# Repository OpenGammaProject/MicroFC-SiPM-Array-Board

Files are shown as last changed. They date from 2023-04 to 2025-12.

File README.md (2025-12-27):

# MicroFC SiPM Array Board

Carrier board for a 2 x 2 array of the 6 mm C-Series MICROFC-60035-SMT silicon photomultipliers by [onsemi](https://www.onsemi.com/pdf/datasheet/microc-series-d.pdf).

PCB size is 20 x 20 mm. The solder pads for the SiPM are slightly bigger than they need to so that you can easily hand-solder everything! I set up a project page over at PCBWay with all the files for you to make it hopefully as easy as possible to order (affiliate link).

<a href="https://www.pcbway.com/project/shareproject/MicroFC_SiPM_Array_Board_8e6e9394.html">PCB from PCBWay</a>

<p align="center">
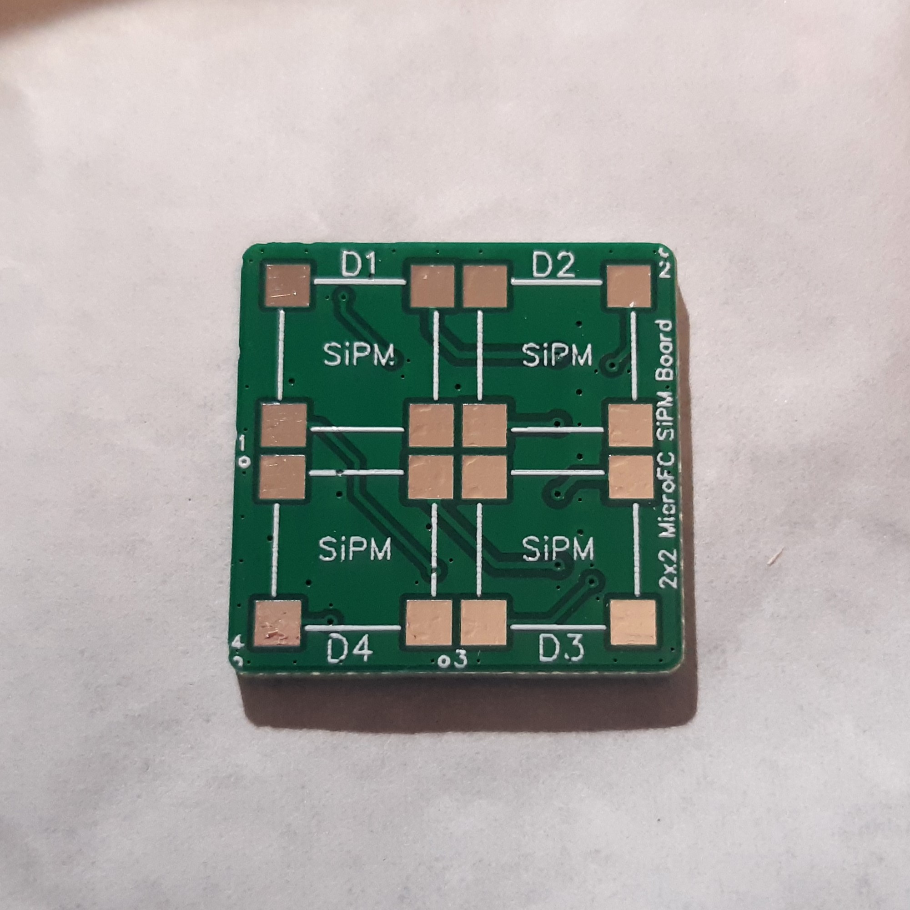
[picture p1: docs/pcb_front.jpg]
Front Side PCB
  
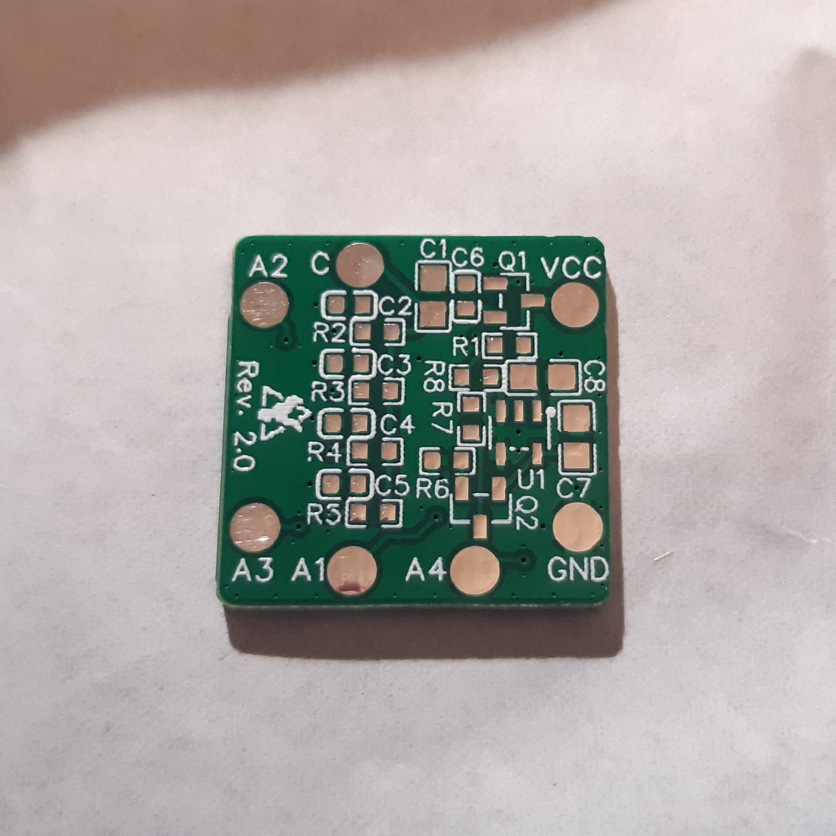
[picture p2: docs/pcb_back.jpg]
Back Side PCB
  
</p>

<p align="center">
  Front Side PCB Rendering
  Back Side PCB Rendering
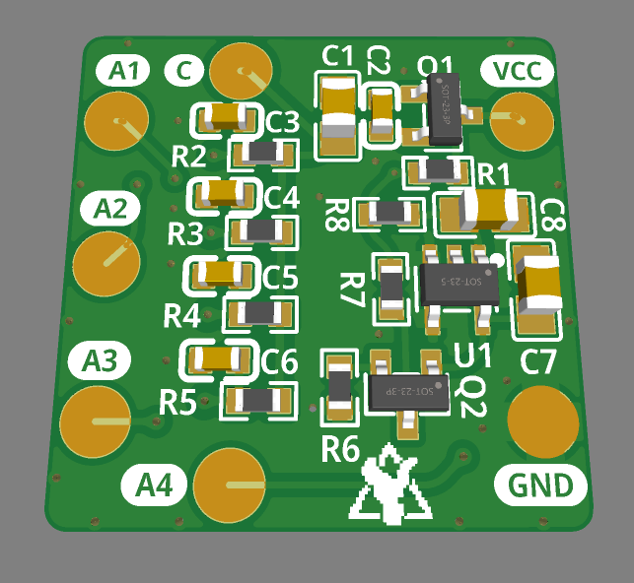
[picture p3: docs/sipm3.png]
Back Side 3D Rendering
  
</p>

On the front side there are only the 4 sensors themselves while all the other parts are on the back. This ensures good optical contact and light-tight sealing. The PCB includes some bias filtering for the 4 SiPMs that must also be soldered and an optional temperature compensation circuit! The temperature compensation takes care of the change in bias voltage and therefore gain depending on the ambient temperature (~21mV/K).

If you want to use the added temperature compensation, be sure to solder all the components to the board and connect your power to the `VCC` pad. For setting the correct voltage, you can check the `C` pad on the PCB, but be sure to do this either before soldering the SiPMs or only when the SiPMs are not exposed to ANY light, otherwise they'll saturate immediately and pass a high current. You can also check the voltage on your power supply itself of course, but due to the nature of the compensation circuitry, the applied voltage to the SiPMs will then be a couple of 100 millivolts lower than what is shown. If you don't want to use the extra circuitry, you can apply your power directly to the `C` pad on the PCB. However, you still need to solder the low-pass filters for that (R2 - R5 and C2 - C5) and C1. The voltage will then be exactly what you apply.

The SiPMs all share a common cathode with bulk decoupling and an R-C low-pass filter each. The anodes are **not** connected together so that you can have some spatial resolution if you want to. You could mount a very small scintillator to each sensor and then have a four pixel gamma-ray camera, yay I guess?!

However, you can also connect all four SiPMs in parallel to a common output by connecting the anode pads to each other, e.g. by connecting the wires that you solder to the pads. You will obviously lose any spatial resolution, but this way you can use it just like a single SiPM in the 4P configuration. SNR should be pretty much the same as with a single SiPM, but your active area will be 4x that of a single one!

To orient the SiPM correctly, look at the notches at the side of the plastic casing. There are 2 lines at the dot right here, that must be matched up with the dot on the PCB. There are numbered dots on the PCB that have to be matched up with that.

<p align="center">
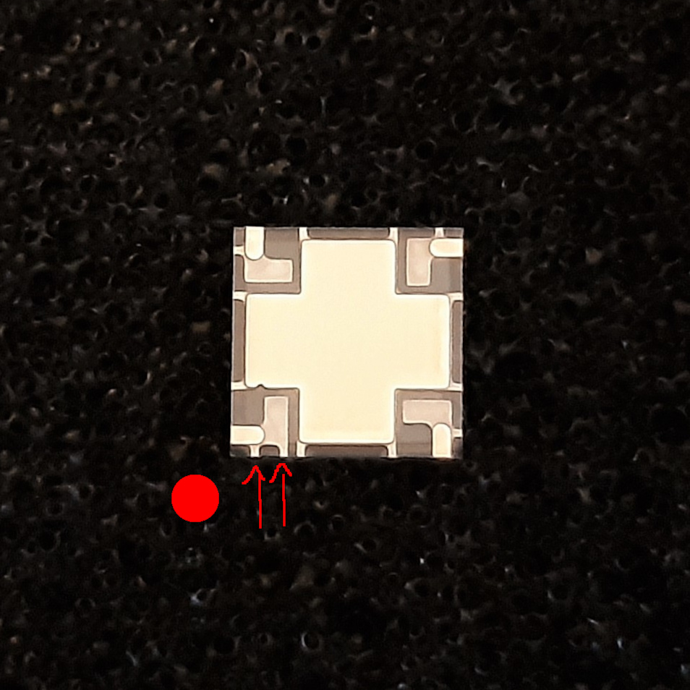
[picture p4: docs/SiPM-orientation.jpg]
SiPM Orientation
  
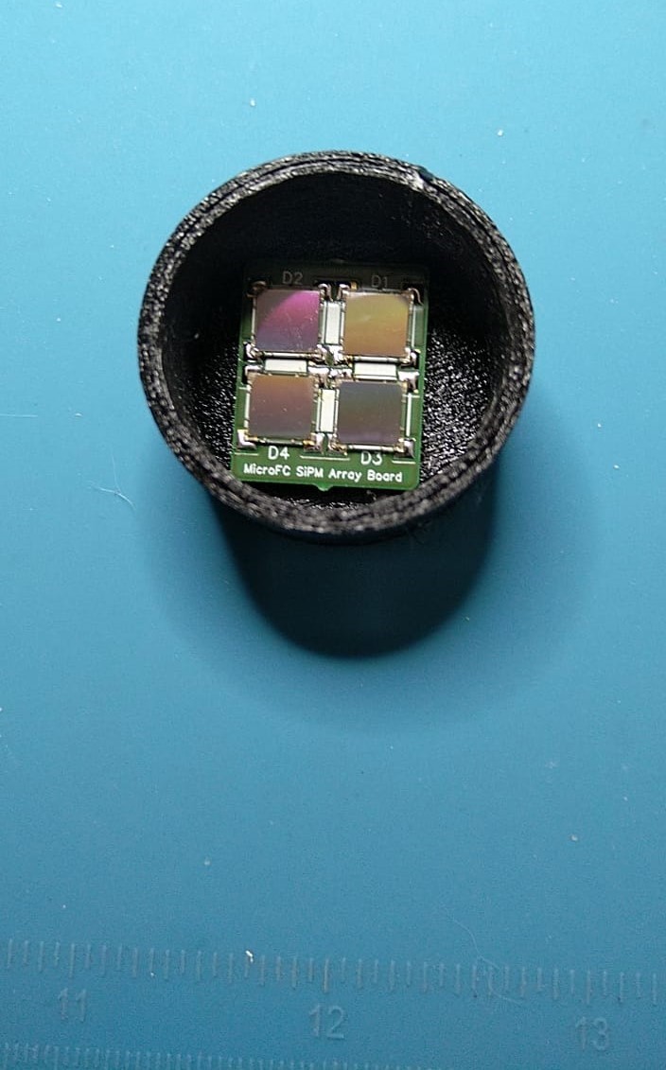
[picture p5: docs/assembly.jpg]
Assembled SiPM array board
  
</p>



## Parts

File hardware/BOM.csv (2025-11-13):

ID | Name | Designator | Footprint | Quantity | Manufacturer Part | Manufacturer | Supplier | Supplier Part | Price
1 | 24kΩ | R1 | R0603 | 1 | AR03BTCX2402 | Viking(光颉) | LCSC | C319717 | 0.03
2 | 49.9Ω | R3,R4,R5,R2 | R0603 | 4 | 0603WAF499JT5E | UNI-ROYAL(厚声) | LCSC | C23185 | 0.001
3 | 4.7uF | C1,C7,C8 | C0805 | 3 | CL21A475KBQNNNE | SAMSUNG(三星) | LCSC | C98192 | 0.02
4 | MMBT5088LT1G | Q1,Q2 | SOT-23-3_L2.9-W1.3-P1.90-LS2.4-BR | 2 | MMBT5088LT1G | onsemi(安森美) | LCSC | C232555 | 0.054
5 | 49.9kΩ | R6,R7 | R0603 | 2 | RT0603BRD0749K9L | YAGEO(国巨) | LCSC | C705780 | 0.024
6 | 10KΩ | R8 | R0603 | 1 | NTCS0603E3103FLT | VISHAY(威世) | LCSC | C142556 | 0.324
7 | TPS7B6950DBVR | U1 | SOT-23-5_L3.0-W1.7-P0.95-LS2.8-BL | 1 | TPS7B6950DBVR | TI(德州仪器) | LCSC | C174327 | 0.455
8 | 100nF | C2,C3,C4,C5,C6 | C0603 | 5 | CL10B104KC8NNNC | SAMSUNG(三星) | LCSC | C15725 | 0.006
9 | SiPM | D1,D2,D3,D4 | MICROFC−60035−SMT | 4 |  | ON Semiconductor | Mouser | 863-MFC60035SMTTR1

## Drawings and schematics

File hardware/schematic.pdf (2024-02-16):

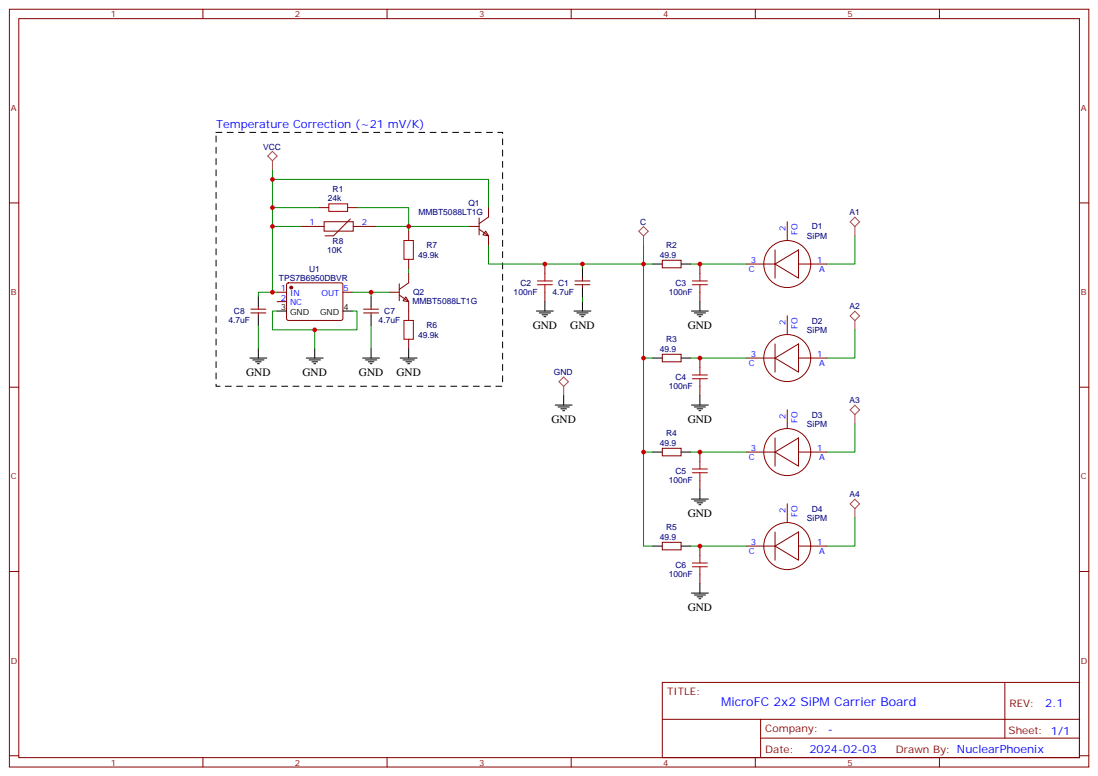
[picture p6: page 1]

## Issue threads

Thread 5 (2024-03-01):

### ISSUE TITLE
Schematics missing

### ISSUE THREAD

**Issue by ProstetnikVogonJeltz** [OpenGammaProject/MicroFC-SiPM-Array-Board#5]
Hi Matthias,

tried to get the Gerbers of V 2.1 processed at JLCPCB, but they complained, that the VIAs are too small (need 0,5/0,25mm) and they 
would have to add Kelvin-Tests (that would add 33€ to a 2€ PCB).
So I decided, to use the PCB-Data provided at Kitspace, but unfortunately it is Rev. 1.0.
Is it possible, to get the Schematics/PCB files for EasyEDA?

Best regards
Uli

**Comment by NuclearPhoenixx** [comment]
Hi there Uli,

looks like I messed up. Accidentally, there were 2 vias with 0.25mm drill hole size, all the others are >0.3mm large. I fixed that for you in the latest Gerber file.

Cheers!

**Comment by ProstetnikVogonJeltz** [comment]
Hallo Matthias,super, vielen lieben Dank dafür 😉!Schöne GrüßeUliAm 01.03.2024 um 12:04 schrieb Matthias ***@***.***>: 
Closed #5 as completed.

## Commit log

2023-04-13 add HW files
    [BOM.csv, Drill_PTH_Through.DRL, Drill_PTH_Through_Via.DRL, Gerber_BoardOutlineLayer.GKO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]
2023-04-27 add assembly photo
2023-11-24 add revision 2
    [BOM.csv, Drill_PTH_Through.DRL, Drill_PTH_Through_Via.DRL, Gerber_BoardOutlineLayer.GKO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]
2023-11-24 fix gerber folder name+
    [Drill_PTH_Through.DRL, Drill_PTH_Through_Via.DRL, Gerber_BoardOutlineLayer.GKO, Gerber_BottomLayer.GBL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]
2023-11-24 fix vias
    [Drill_PTH_Through.DRL, Drill_PTH_Through_Via.DRL, Gerber_BoardOutlineLayer.GKO, Gerber_BottomLayer.GBL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]
2023-11-24 [ImgBot] Optimize images
    *Total -- 292.28kb -> 208.88kb (28.53%)
    /docs/sipm1.png -- 62.88kb -> 20.56kb (67.3%)
    /docs/sipm2.png -- 83.40kb -> 47.81kb (42.67%)
    /docs/assembly.jpg -- 146.00kb -> 140.50kb (3.77%)
2023-12-27 [ImgBot] Optimize images
    *Total -- 1,055.99kb -> 996.47kb (5.64%)
    /docs/pcb_front.jpg -- 538.33kb -> 506.46kb (5.92%)
    /docs/pcb_back.jpg -- 517.66kb -> 490.01kb (5.34%)
2024-02-16 add rev 2.1 files
    [BOM.csv, Drill_PTH_Through.DRL, Drill_PTH_Through_Via.DRL, Gerber_BoardOutlineLayer.GKO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]
2024-03-01 Fix via size
    [Drill_PTH_Through.DRL, Drill_PTH_Through_Via.DRL, Gerber_BoardOutlineLayer.GKO, Gerber_BottomLayer.GBL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]
2025-02-22 add pick and place file
    [PickAndPlace_PCB.csv]
2025-11-13 fix hardware files
    [BOM.csv, Drill_PTH_Through.DRL, Drill_PTH_Through_Via.DRL, Gerber_BoardOutlineLayer.GKO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]
2025-12-27 add pcbway project page
